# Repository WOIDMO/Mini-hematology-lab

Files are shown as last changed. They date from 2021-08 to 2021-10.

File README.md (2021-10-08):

# Mini-hematology-lab
Open Source Mini Hematology Lab

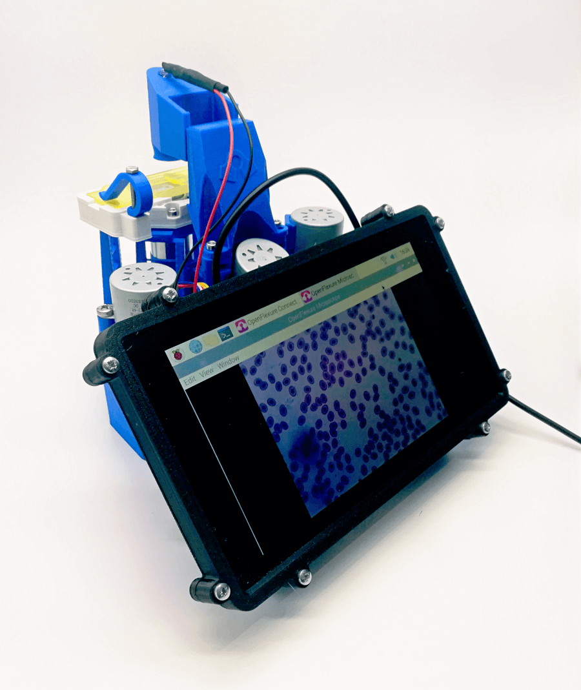
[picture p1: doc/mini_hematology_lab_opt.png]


The use of flow cytometry for common blood analysis in developing countries and field laboratories is problematic due to the high cost of the equipment, limited access to servicing and unreliable power. As an alternative to this technique we are developping a deep-learning AI powered microscope for analysis of blood and other samples.

Manual microscopy has served as a bedrock for many modern diagnostics, including diagnosing diseases such as Malaria. Direct visual identification of blood cells remains the gold standard for numerous diseases. However, this comes at the cost of tedious labor and human errors. Human fatigue has been identified as a crucial factor in reduced efficiency in microscopy based diagnostics. The same technological advancements that will one day lead to self-driving cars is currently mature enough to take over this task.

Based on the openflexure robotic microscope, we are developing a low-cost 3D printable autonomous platform capable of counting blood cell types and detecting parasite infections through the application of machine-learning. The device allows screening of more than 1.5 million red blood cells per minute for infections, which is 120 times faster compared to traditional manual microscopy. The cost of constructing the mini hematology lab is expected to be below 350 USD.

**Features:**

* Red blood cell count (RBC)
* White blood cell count (WBC)
* Differential white blood cell count
* Platelet count
* Parasite detection (eg Malaria)
* Battery powered (USB)
* Low cost

**Documentation:**

Please refer to the [wiki](https://github.com/WOIDMO/Mini-hematology-lab/wiki) 

**Progress:**

* 2021-09-01 Microscope design modifications: done
* 2021-10-01 Motor controller board design: done
* 2021-10-04 Blood staining protocol and started wiki: done
* 2021-xx-xx Software for AI hematology: pending
* 2021-xx-xx Software for AI malaria: pending
* 2021-xx-xx Documentation: pending

**Credits:**

The microscope is based on the [OpenFlexure](https://openflexure.org/) project started by Richard Bowman and maintained by the Bath Open INstrumentation Group.

The microscope is being extended for field and automated diagnostic use by the [WoIdMo](https://woidmo.org).

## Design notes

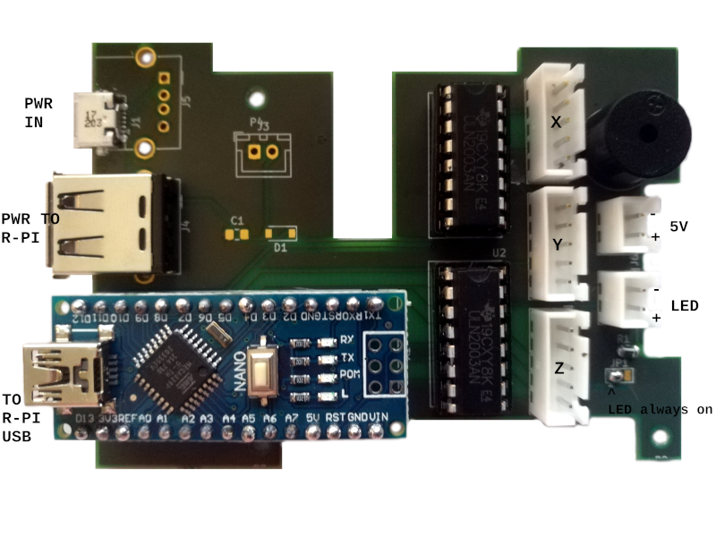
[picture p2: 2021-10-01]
motor_controller/driver_board_img.png

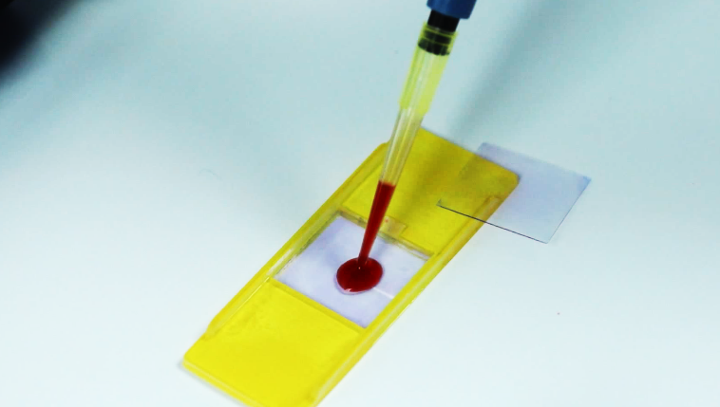
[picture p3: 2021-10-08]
counting_chamber/Counting_chamber.png

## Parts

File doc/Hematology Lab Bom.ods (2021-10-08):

Mini Hematology Lab - Bill of Materials
Item | Supplier | Cat# | Unit cost (EUR) | Amount | Subtotal (EUR)
PLA | Aliexpress |  | 10.00 | 1 | 10.00
M3x25mm Hex head - Inox | rvspaleis.nl | 933-2-3x25 | 0.16 | 2 | 0.32
M3 Hex nut - Inox | rvspaleis.nl | 934-2-3 | 0.16 | 4 | 0.64
M3x8mm Cap head - Inox | rvspaleis.nl | 912-2-3x8 | 0.16 | 8 | 1.28
M3 Washer - Inox | rvspaleis.nl | 125-2-3_250 | 0.01 | 16 | 0.16
M4x6mm Cap head - Inox | rvspaleis.nl | 7985-2-4x6 | 0.16 | 18 | 2.88
M4 Hex nut - Inox | rvspaleis.nl | 0934-2-4 | 0.16 | 4 | 0.64
M2x6mm Button head - Inox | rvspaleis.nl | 7985-2-2x6 | 0.16 | 4 | 0.64
Viton o-ring 30x2mm - FKM - FPM - Viton - 80 Shore A -Black | www.o-ring-stocks.eu | ORS23647 | 0.47 | 3 | 1.41
LED 5mm White (high brightness) | Aliexpress |  | 0.01 | 1 | 0.01
Stranded wire | Aliexpress |  | 2.00 | 1 | 2.00
JST connector 2p | Aliexpress |  | 0.10 | 1 | 0.10
Raspberry camera V2 | rs-online.com | 111-5551 | 25.13 | 1 | 25.13
Raspberry Pi4B 8GB | rs-online.com | 182-2098 | 81.99 | 1 | 81.99
Raspberry touch display | rs-online.com | 899-7466 | 68.33 | 1 | 68.33
SD card 16GB | Aliexpress |  | 3.20 | 1 | 3.20
Micro stepper 28BYJ-48 | Aliexpress |  | 2.60 | 3 | 7.80
Arduino Nano | Aliexpress |  | 3.08 | 1 | 3.08
LED lens D13mm FL5mm | Aliexpress |  | 0.28 | 1 | 0.28
Double cemented lens D12.7mm FL50mm | Aliexpress |  | 21.00 | 1 | 21.00
Microscope objective (160/60x) | Aliexpress |  | 29.00 | 1 | 29.00
PCB motor controller (min order 3) | aisler.net |  | 8.96 | 1 | 8.96
ASSMANN WSW 2.54mm Pitch Vertical 16 Way, Through Hole Stamped Pin Open Frame IC Dip Socket, 1A | rs-online.com | 674-2432 | 0.28 | 2 | 0.56
JST, XH, B5B, 5 Way, 1 Row, Straight PCB Header | rs-online.com | 820-1560 | 0.53 | 3 | 1.59
JST, XH, B2B, 2 Way, 1 Row, Straight PCB Header | rs-online.com | 820-1554 | 0.16 | 2 | 0.32
Molex, Right Angle, Through Hole, Socket Type A USB Connector | rs-online.com | 800-6839 | 1.55 | 1 | 1.55
Molex, Right Angle, SMT, Socket Type Micro AB 2.0 USB Connector | rs-online.com | 702-5481 | 0.90 | 1 | 0.90
5V buzzer 12x9.5mm | Aliexpress |  | 0.16 | 1 | 0.16
60R SMD0508 | rs-online.com | 717-2130 | 0.01 | 1 | 0.01
Header for the arduino socket | Aliexpress |  | 0.10 | 1 | 0.10
Hex pcb spacer 20mm M2.5 | Aliexpress |  | 0.30 | 4 | 1.20
USB C cable 2.4A 25cm | Aliexpress |  | 2.07 | 1 | 2.07
Gear grease 10g (tube grease for 3d printer) | Aliexpress |  | 1.63 | 1 | 1.63
 |  |  |  | Total (EUR) | 278.94

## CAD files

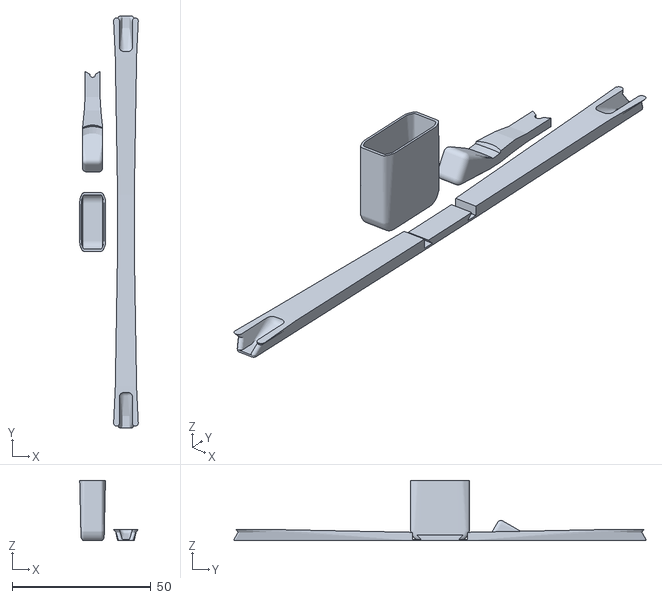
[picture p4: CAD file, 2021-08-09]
stl/actuator_assembly_tools.stl
21.1 x 148.2 x 21.7

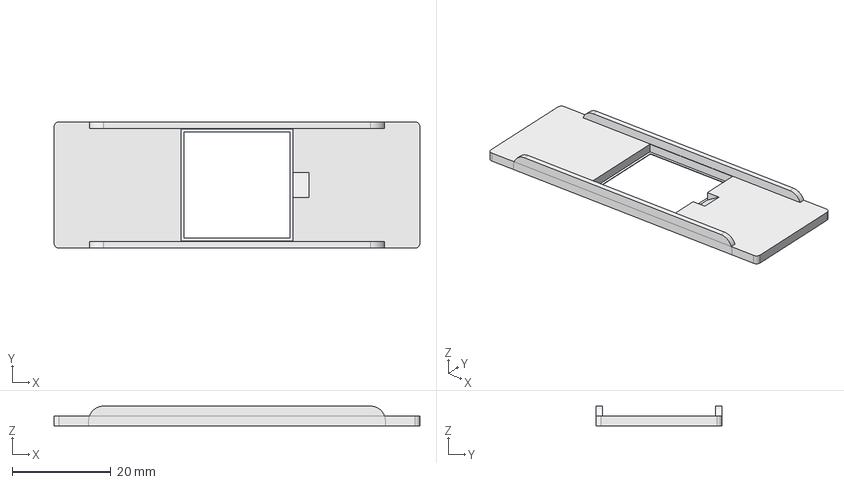
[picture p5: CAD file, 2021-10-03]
counting_chamber/counting_chamber_v6.FCStd
74.0 x 25.5 x 4.00 mm

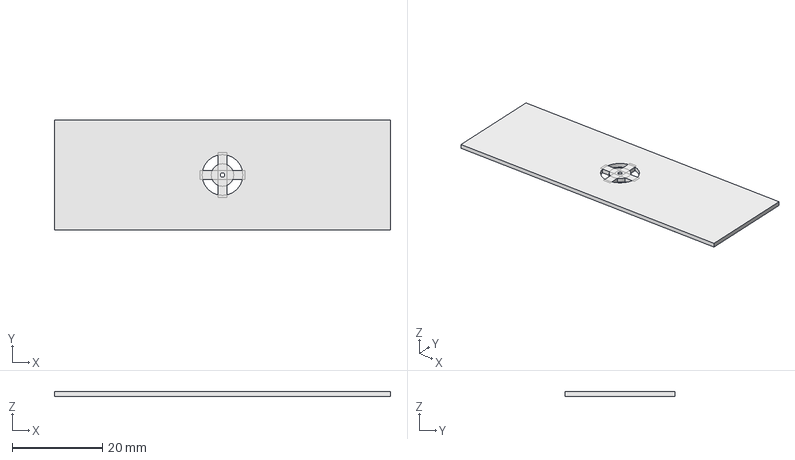
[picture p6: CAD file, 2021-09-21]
stl/Slide_center.FCStd
74.5 x 24.5 x 1.00 mm

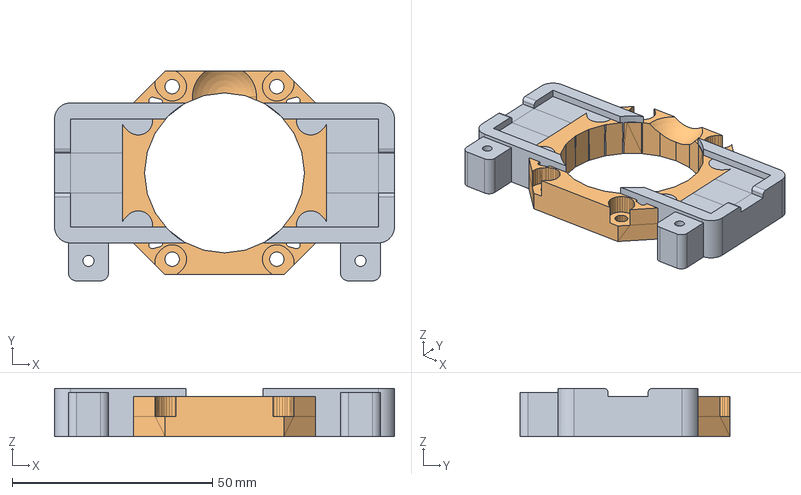
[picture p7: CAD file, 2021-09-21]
stl/Slide_stage_V1.FCStd
85.0 x 52.5 x 12.0 mm

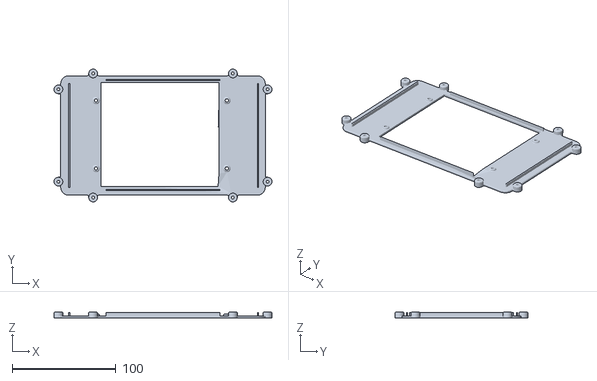
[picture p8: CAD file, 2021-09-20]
stl/screen_back.stl
210.5 x 128.3 x 5.50

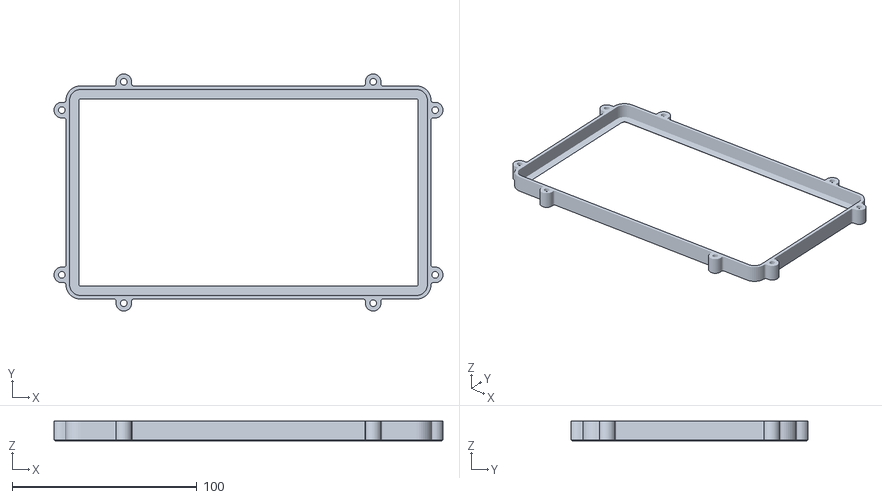
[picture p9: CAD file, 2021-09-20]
stl/RTS-FRAME.STL
210.4 x 128.2 x 10.6

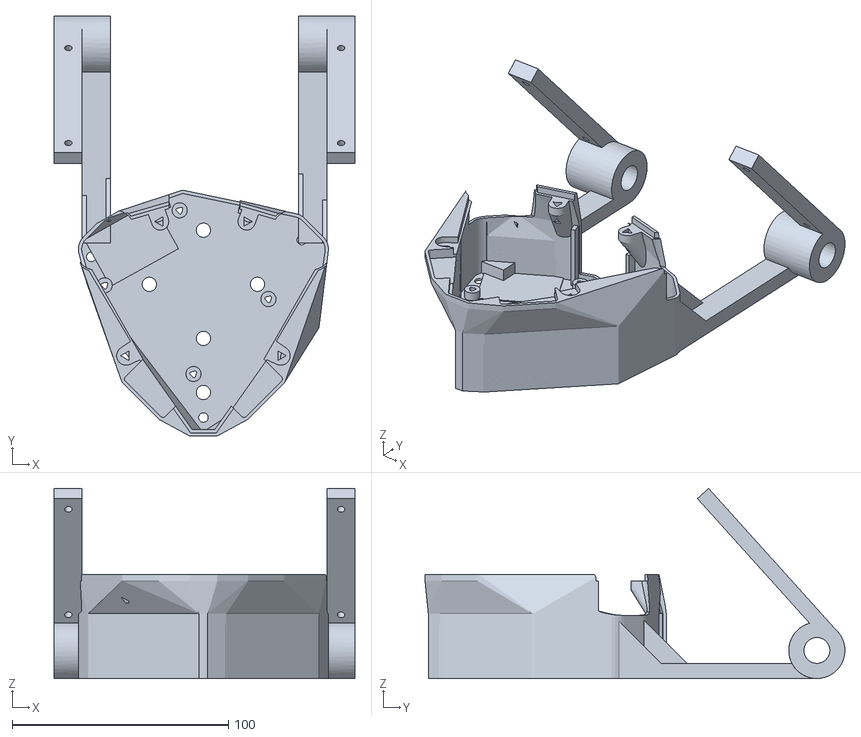
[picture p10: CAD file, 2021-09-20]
stl/Microscope_stand_screen_v2.stl
139.0 x 194.1 x 87.9

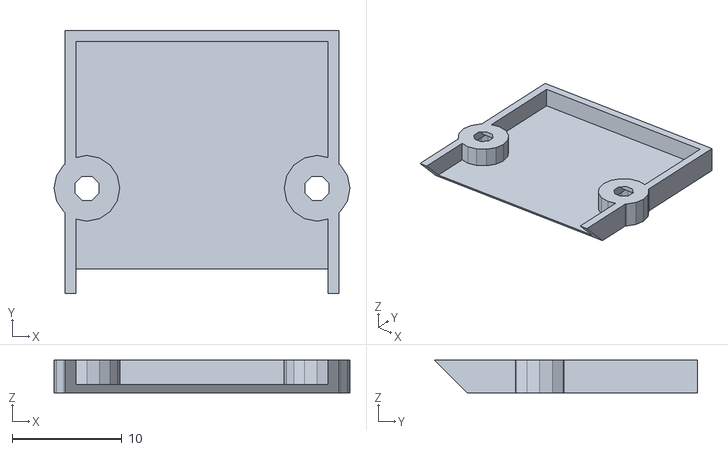
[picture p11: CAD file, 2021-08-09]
stl/picamera_2_cover.stl
27.0 x 24.0 x 3.00

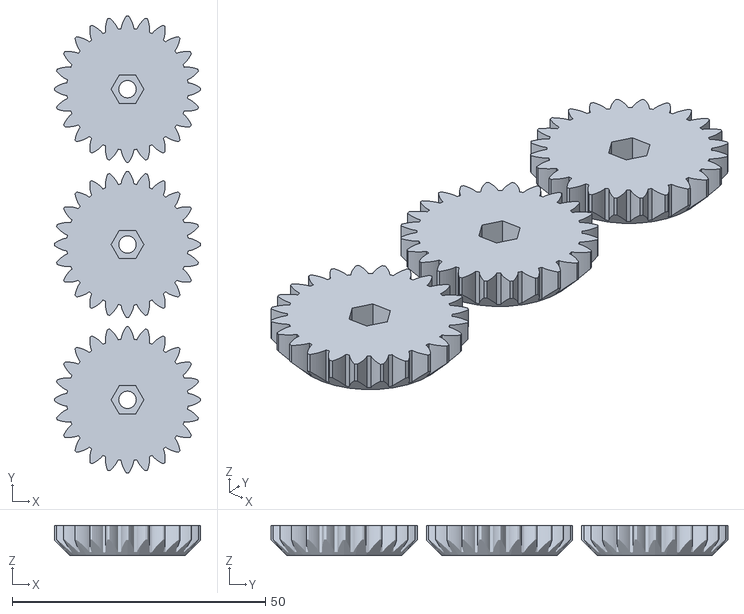
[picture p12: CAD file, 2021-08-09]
stl/gears.stl
28.9 x 90.2 x 6.00

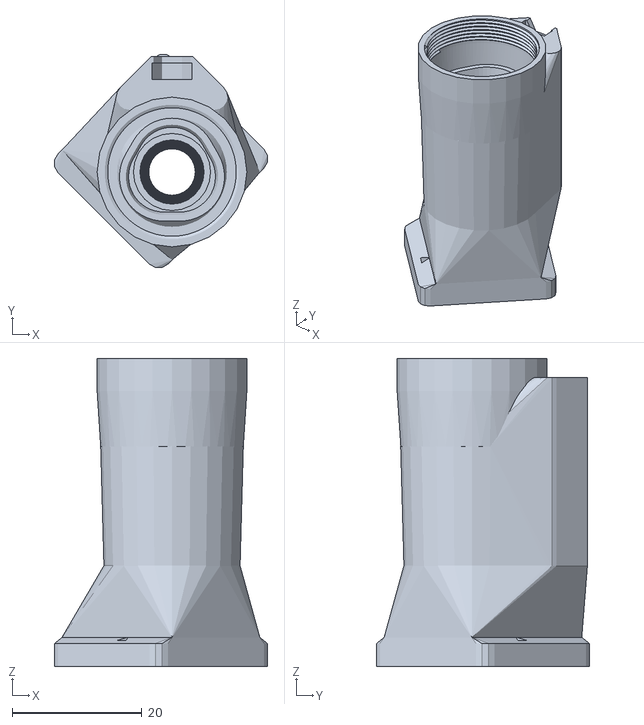
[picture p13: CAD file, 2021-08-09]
stl/optics_picamera_2_rms_f50d13.stl
32.9 x 32.9 x 47.5

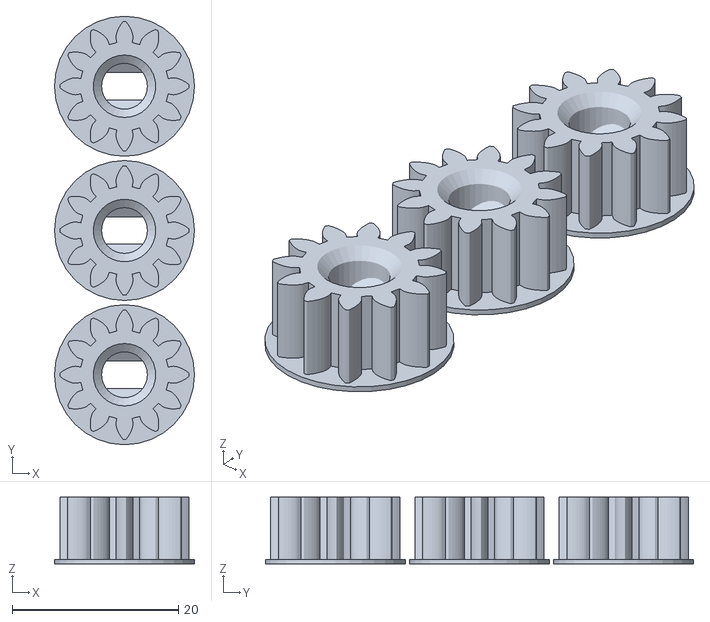
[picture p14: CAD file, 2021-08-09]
stl/small_gears.stl
16.8 x 51.5 x 8.00

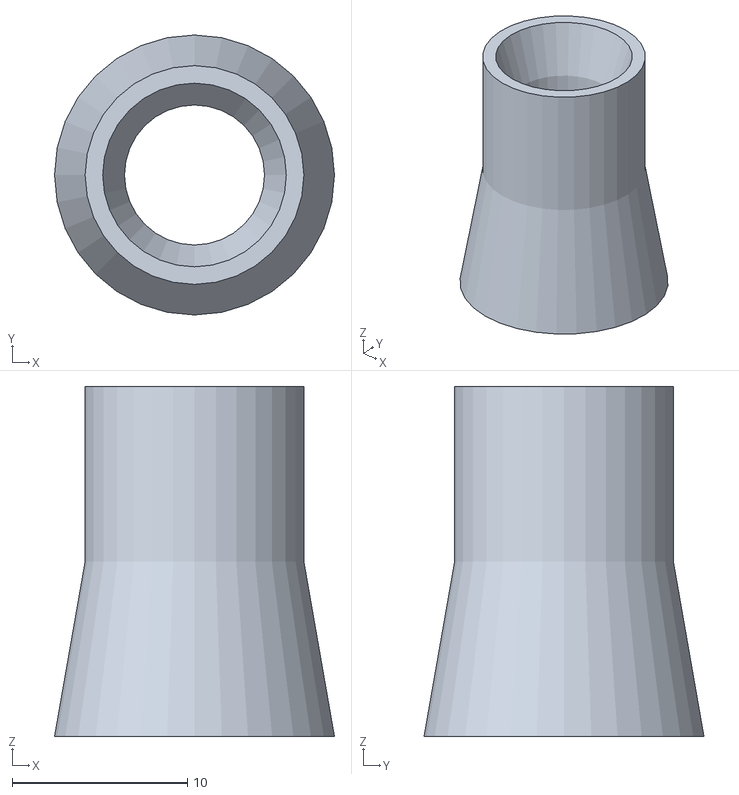
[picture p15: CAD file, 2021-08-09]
stl/lens_tool.stl
16.0 x 16.0 x 20.0

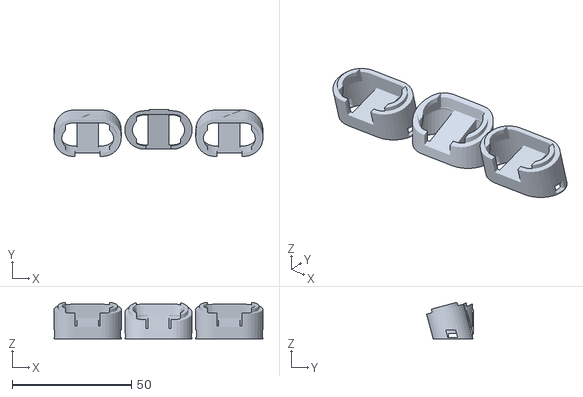
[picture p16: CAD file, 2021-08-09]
stl/feet.stl
87.6 x 19.7 x 15.3

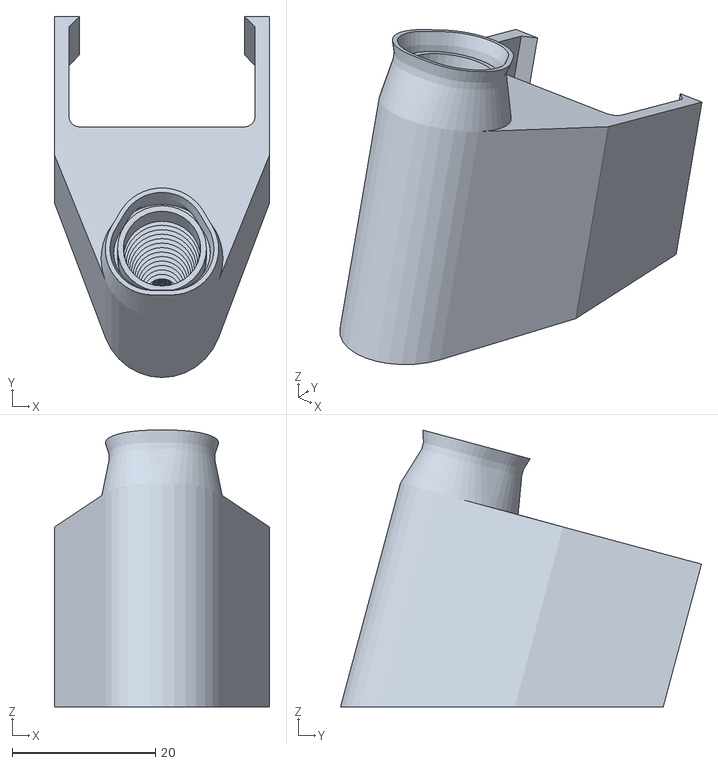
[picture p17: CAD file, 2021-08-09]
stl/condenser.stl
30.0 x 50.4 x 38.6

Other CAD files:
stl/illumination_dovetail.stl
counting_chamber/counting_chamber_v6.stl
stl/Slide_center.stl
stl/slide_stage_V1.stl

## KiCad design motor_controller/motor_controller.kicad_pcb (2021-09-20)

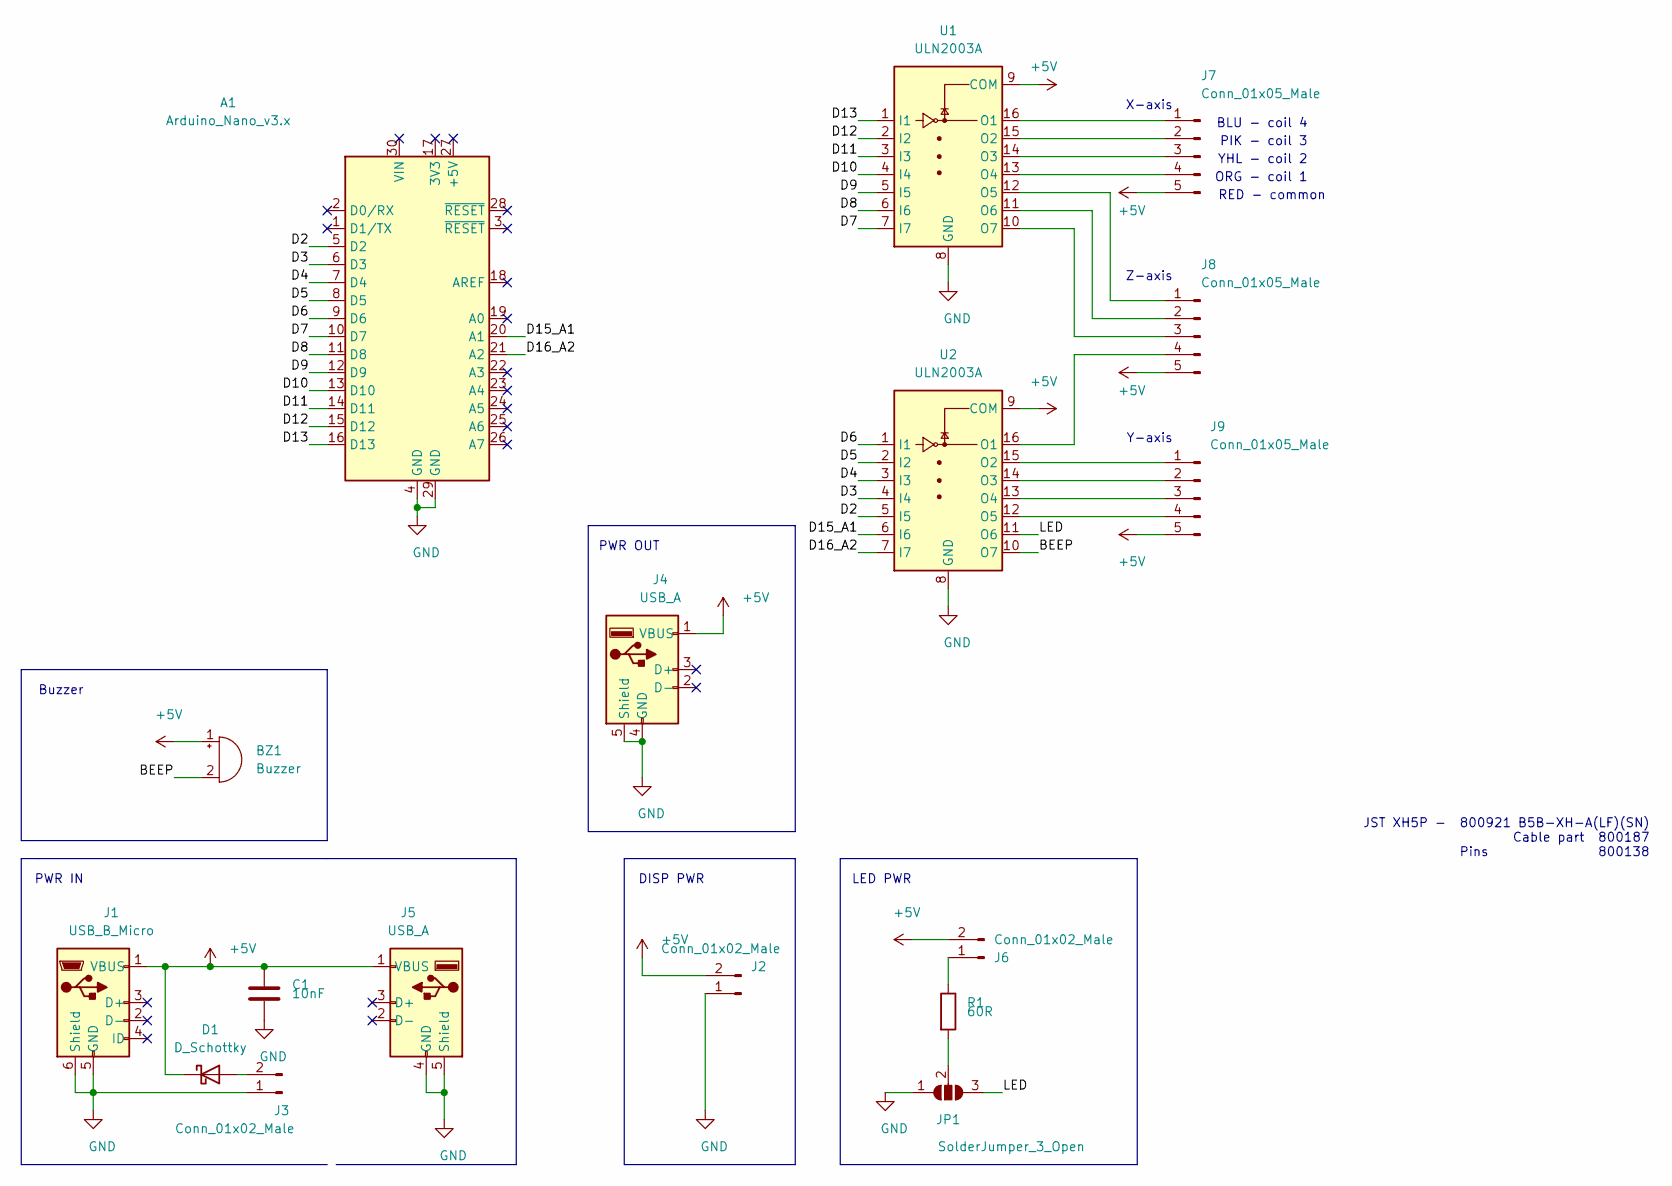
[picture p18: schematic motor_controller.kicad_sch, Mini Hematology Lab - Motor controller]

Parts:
A1: Arduino_Nano_v3.x; Arduino_Nano
BZ1: Buzzer; Buzzer_12x9.5RM7.6
C1: 10nF; C_0805_2012Metric_Pad1.15x1.40mm_HandSolder
D1: D_Schottky; D_SOD-123
J1: USB_B_Micro; USB_Micro-AB_Molex_47590-0001
J2, J3, J6: Conn_01x02_Male; JST_XH_B2B-XH-A_1x02_P2.50mm_Vertical
J4, J5: USB_A; USB_A_Molex_67643_Horizontal
J7, J8, J9: Conn_01x05_Male; JST_XH_B5B-XH-A_1x05_P2.50mm_Vertical
JP1: SolderJumper_3_Open; SolderJumper-3_P1.3mm_Open_Pad1.0x1.5mm
R1: 60R; R_0805_2012Metric_Pad1.15x1.40mm_HandSolder
U1, U2: ULN2003A; DIP-16_W7.62mm_Socket

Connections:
+5V: BZ1.1 (-), C1.1, D1.1 (K), J1.1 (VBUS), J2.2, J4.1 (VBUS), J5.1 (VBUS), J6.2, J7.5, J8.5, J9.5, U1.9 (COM), U2.9 (COM)
/BEEP: BZ1.2 (+), U2.10 (O7)
/D2: A1.5 (D2), U2.5 (I5)
/D3: A1.6 (D3), U2.4 (I4)
/D4: A1.7 (D4), U2.3 (I3)
/D5: A1.8 (D5), U2.2 (I2)
/D6: A1.9 (D6), U2.1 (I1)
/D7: A1.10 (D7), U1.7 (I7)
/D8: A1.11 (D8), U1.6 (I6)
/D9: A1.12 (D9), U1.5 (I5)
/D10: A1.13 (D10), U1.4 (I4)
/D11: A1.14 (D11), U1.3 (I3)
/D12: A1.15 (D12), U1.2 (I2)
/D13: A1.16 (D13), U1.1 (I1)
/D15_A1: A1.20 (A1), U2.6 (I6)
/D16_A2: A1.21 (A2), U2.7 (I7)
/LED: JP1.3 (B), U2.11 (O6)
GND: A1.4 (GND), A1.29 (GND), C1.2, J1.5 (GND), J1.6 (Shield), J2.1, J3.1, J4.4 (GND), J4.5 (Shield), J5.4 (GND), J5.5 (Shield), JP1.1 (A), U1.8 (GND), U2.8 (GND)
unnamed: D1.2 (A), J3.2
unnamed: J6.1, R1.1
unnamed: J7.1, U1.16 (O1)
unnamed: J7.2, U1.15 (O2)
unnamed: J7.3, U1.14 (O3)
unnamed: J7.4, U1.13 (O4)
unnamed: J8.1, U1.12 (O5)
unnamed: J8.2, U1.11 (O6)
unnamed: J8.3, U1.10 (O7)
unnamed: J8.4, U2.16 (O1)
unnamed: J9.1, U2.15 (O2)
unnamed: J9.2, U2.14 (O3)
unnamed: J9.3, U2.13 (O4)
unnamed: J9.4, U2.12 (O5)
unnamed: JP1.2 (C), R1.2

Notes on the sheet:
Buzzer
PWR IN
PWR OUT
DISP PWR
LED PWR
X-axis
Z-axis
Y-axis
BLU - coil 4
PIK - coil 3
YHL - coil 2
ORG - coil 1
RED - common
JST XH5P - 800921 B5B-XH-A(LF)(SN) Cable part 800187 Pins 800138

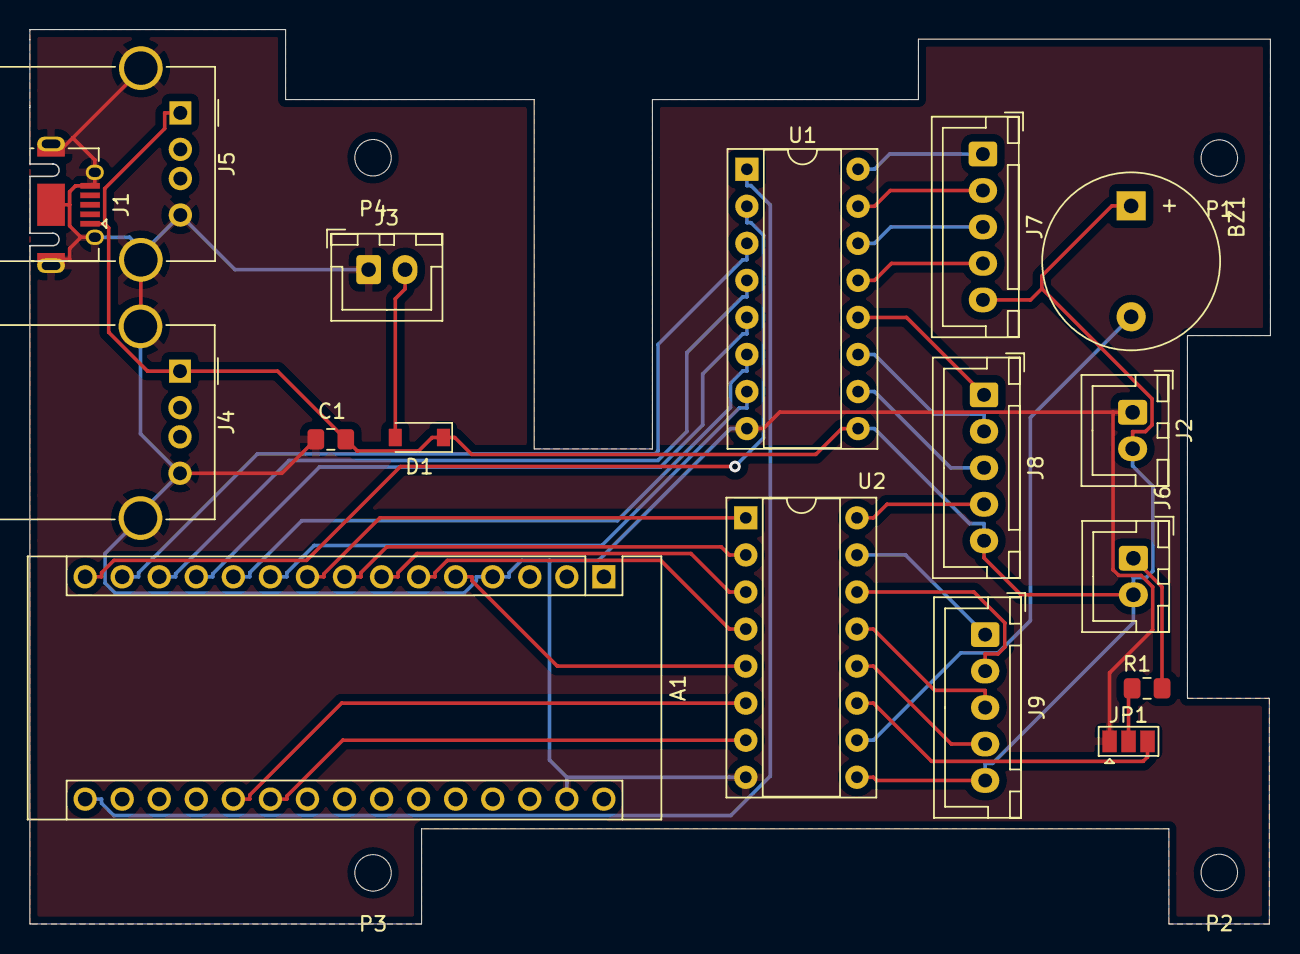
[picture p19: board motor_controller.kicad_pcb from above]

Board: 2 copper layers, 85.0 x 61.3 mm, 21 parts (0 on the bottom side), 33 nets.

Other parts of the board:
P1, P2, P3, P4: MountingHole_2.5mm

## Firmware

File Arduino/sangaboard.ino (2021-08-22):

/*
 * Sangaboard firmware
 * 
 * Most of the code is reused from the old openflexure_nano_motorcontroller firmware
 * 
 * This firmware was written by
 * Richard Bowman
 * Julian Stirling
 * Boyko Vodenicharski
 * Filip Ayazi
 * 
 * Much of the code is based on older code written by
 * James Sharkey and Fergus Riche
 * 
 * Released under GPL v3, 2017
 */
#include "StepperF_alt.h"   //Fergus's hacked stepper library
#include <assert.h>
#include <EEPROM.h>
#include <limits.h>

// LIGHT SENSOR SUPPORT
// Uncomment (exactly) one of the lines below to enable support for that sensor.
//#define ADAFRUIT_TSL2591
//#define ADAFRUIT_ADS1115

#ifdef ADAFRUIT_TSL2591
#include <Wire.h>
#include <Adafruit_Sensor.h>
#include <Adafruit_TSL2591.h>
#define LIGHT_SENSOR
#endif
#ifdef ADAFRUIT_ADS1115
#include <Wire.h>
#include <Adafruit_ADS1015.h>
#define LIGHT_SENSOR
#endif

//debug serial prints
#define DEBUG_ON

#ifdef DEBUG_ON
  #define D(x)  Serial.println (x)
#else
  #define D(x)
#endif


/*
 ************
 * ENDSTOPS *
 ************
*/
//#define ENDSTOPS_MIN
//#define ENDSTOPS_MAX

#if defined(ENDSTOPS_MIN) || defined(ENDSTOPS_MAX)
  //endstops are closed when the pin is down  by default, this inverts the behaviour
  #define ENDSTOPS_INVERT false

  #define ENDSTOPS_PULLUPS true

  //soft endstops trigger when 0/MAX is reached in the direction without endstops
  #define ENDSTOPS_SOFT

  //endstops wiring and positions
  const int endstops_min[]={A0,A1,A2};
  const int endstops_max[]={A3,A4,A5};
  long axis_max[3];
#endif

#ifdef ARDUINO_AVR_LEONARDO
  #define SANGABOARDv3
  #define BOARD_STRING "Sangaboard v0.3"
#elif ARDUINO_AVR_SANGABOARD
  #define SANGABOARDv3
  #define BOARD_STRING "Sangaboard v0.3"
#else
  #define SANGABOARDv2
  #define BOARD_STRING "Sangaboard v0.2"
#endif

#define EACH_MOTOR for(int i=0; i<n_motors; i++)
#define VER_STRING "Sangaboard Firmware v0.5.1"

// The array below has 3 stepper objects, for X,Y,Z respectively
const int n_motors = 3;
long min_step_delay;
const int min_step_delay_eeprom = sizeof(long)*n_motors;
long ramp_time;
const int ramp_time_eeprom = sizeof(long)*(n_motors+1);
const int axis_max_eeprom = sizeof(long)*(n_motors+2);
Stepper* motors[n_motors];
signed long current_pos[n_motors];
long steps_remaining[n_motors];

bool test_mode=false;

// We'll use this input buffer for serial comms
const int INPUT_BUFFER_LENGTH = 64;
char input_buffer[INPUT_BUFFER_LENGTH];

int command_prefix(String command, const char ** prefixes, int n_prefixes){
  // Check if the command starts with any of the prefixes in the list.
  // returns the index if so, otherwise returns -1
  for(int i=0; i<n_prefixes; i++){
    if(command.startsWith(prefixes[i])){
      return i;
    }
  }
  return -1;
}

void setup() {
  // initialise serial port
  Serial.begin(115200);
  while (! Serial )
    delay(1);
  // get the stepoper objects from the motor shield objects
  #if defined(SANGABOARDv2)
    motors[0] = new Stepper(8, 13, 12, 11, 10);
    motors[1] = new Stepper(8, 9, 8, 7, 6);
    motors[2] = new Stepper(8, 5, 4, 3, 2);
  #elif defined(SANGABOARDv3)
    motors[0] = new Stepper(8, 8, 9, 10, 11);
    motors[1] = new Stepper(8, 5, 13, 4, 12);
    motors[2] = new Stepper(8, 6, 7, A5, A4);
  #endif
  EACH_MOTOR{
    motors[i]->setSpeed(10); // as a default set to 10 rpm, though this is ignored...
    steps_remaining[i]=0;
    EEPROM.get(sizeof(long)*i, current_pos[i]); //read last saved position from EEPROM
    //current_pos[i] = 0; //alternatively, reset on power cycle!
  }

  EEPROM.get(min_step_delay_eeprom, min_step_delay);
  if(min_step_delay < 0){ // -1 seems to be what we get if it's uninitialised.
    min_step_delay = 1000;
    EEPROM.put(min_step_delay_eeprom, min_step_delay);
  }
  EEPROM.get(ramp_time_eeprom, ramp_time);
  if(ramp_time < 0){ // -1 seems to be what we get if it's uninitialised.
    ramp_time = 0;
    EEPROM.put(ramp_time_eeprom, ramp_time);
  }
  #ifdef LIGHT_SENSOR
  setup_light_sensor();
  #endif /* LIGHT_SENSOR */

  #if defined(ENDSTOPS_MIN) || defined(ENDSTOPS_MAX)
    EACH_MOTOR{
      EEPROM.get(axis_max_eeprom+i*sizeof(long), axis_max[i]);
    }
  #endif

  #ifdef ENDSTOPS_MIN
    EACH_MOTOR{
      if(ENDSTOPS_PULLUPS)
        pinMode(endstops_min[i], INPUT_PULLUP);
      else
        pinMode(endstops_min[i], INPUT);
    }
  #endif

  #ifdef ENDSTOPS_MAX
    EACH_MOTOR{
      if(ENDSTOPS_PULLUPS)
        pinMode(endstops_max[i], INPUT_PULLUP);
      else
        pinMode(endstops_max[i], INPUT);
    }
  #endif

  Serial.println(F(VER_STRING));

}


void stepMotor(int motor, long dx){
  //make a single step of a single motor.
  current_pos[motor] += dx;
  motors[motor]->stepMotor(((current_pos[motor] % 8) + 8) % 8); //forgive the double-modulo; I need 0-7 even for -ve numbers
}

void releaseMotor(int motor){
  //release the stepper motor (de-enegrise the coils)
  motors[motor]->stepMotor(8);
}

void print_position(){
  EACH_MOTOR{
    if(i>0) Serial.print(" ");
    Serial.print(current_pos[i]);
  }
  Serial.println();
}

#if defined(ENDSTOPS_MIN) || defined(ENDSTOPS_MAX)

/**
* Check if endstop is triggered, direction {-1,+1} for {min,max} endstop
*/
boolean endstopTriggered(int axis, int direction){
#if defined(ENDSTOPS_MIN)
    if(direction<0){
      int value=analogRead(endstops_min[axis]);
      if(ENDSTOPS_INVERT!=(value<100))
        return true;
    }
#elif defined(ENDSTOPS_SOFT)
    if(direction<0 && current_pos[axis]<1)
        return true;
#endif

#if defined(ENDSTOPS_MAX)
  if(direction>0){
      int value=analogRead(endstops_max[axis]);
      if(ENDSTOPS_INVERT!=(value<100))
        return true;
  }
#elif defined(ENDSTOPS_SOFT)
  if(direction>0 && current_pos[axis]>=axis_max[axis])
    return true;
#endif
  return false;
}

void print_endstops_status(){
   EACH_MOTOR{
    if(i>0) Serial.print(" ");
      if(endstopTriggered(i,-1))
        Serial.print("-1");
      else if(endstopTriggered(i,1))
        Serial.print("1");
      else
    Serial.print("0");
  }
  Serial.println();
}

void print_axes_max(){
  EACH_MOTOR{
    if(i>0) Serial.print(" ");
    Serial.print(axis_max[i]);
  }
  Serial.println();
}

void home_min(){
    byte axes=7; //00000111
    home_min(axes);
}

void home_max(){
  byte axes=7;
  home_max(axes);
}

void home_min(byte axes){
  #ifdef ENDSTOPS_MIN
    int hit=0;
    long shift_min[3];
    long displ[3];

    EACH_MOTOR{
      if(axes&(1<<i)){
        shift_min[i]=3500;
        displ[i]=-100000;
      }else{
        shift_min[i]=0;
        displ[i]=0;
      }
    }

    EACH_MOTOR{
      hit=move_axes(displ);
      displ[-hit-1]=0;
    }

    //if in test mode, print positions when the endstops were hit the first time
    if(test_mode){
      Serial.print("First hits: ");
      print_position();
    }

    move_axes(shift_min);
    //now we should be <shift> steps away in chosen axes, first shift a bit closer
    //as the close and open positions some distance apart, then go
    //slowly back for maximum accuracy
    long shift_back[]={-shift_min[0]/2,-shift_min[1]/2,-shift_min[2]/2};
    move_axes(shift_back);
    delay(200);
    EACH_MOTOR{
      if(axes&(1<<i)){
        while(!endstopTriggered(i,-1)){
          stepMotor(i,-1);
          delayMicroseconds(4000);
        }
        if(test_mode){
          Serial.print("Homed endstop ");
          Serial.print(i);
          Serial.print(":");
          Serial.print(current_pos[i]);
          Serial.println();
        }
        current_pos[i]=0;
      }
    }
    EEPROM.put(0, current_pos);
    //move a little higher so the endstops are released
    if(!test_mode)
      move_axes(shift_min);
  #endif
  Serial.println("done.");
}

// UNTESTED
void home_max(byte axes){
  #ifdef ENDSTOPS_MAX
    //same as above
    int hit=0;
    long shift_max[3];
    long displ[3];
    EACH_MOTOR{
      if(axes&(1<<i)){
        shift_max[i]=-2000;
        displ[i]=150000;
      }else{
        shift_max[i]=0;
        displ[i]=0;
      }
    }

    EACH_MOTOR{
      hit=move_axes(displ);
      displ[hit-1]=0;
    }

    if(test_mode){
      Serial.print("First hits: ");
      print_position();
    }

    move_axes(shift_max);
    long shift_forw[]= {shift_max[0]/2,shift_max[1]/2,shift_max[2]/2};
    move_axes(shift_forw);

    EACH_MOTOR{
      if(axes&(1<<i)){
        while(!endstopTriggered(i,1)){
          stepMotor(i,1);
          delay(150);
        }
        if(test_mode){
          Serial.print("Homed endstop ");
          Serial.print(i);
          Serial.print(":");
          Serial.print(current_pos[i]);
          Serial.println();
        }
        axis_max[i]=current_pos[i];
      }
    }
    EEPROM.put(0, current_pos);
    EEPROM.put(axis_max_eeprom, axis_max);
  #endif
  Serial.println("done.");
}


#endif //ENDSTOPS
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
